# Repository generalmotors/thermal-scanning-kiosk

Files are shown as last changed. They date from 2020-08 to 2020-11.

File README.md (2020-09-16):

## title: Thermal Scanning Kiosk

# Overview and Context

In this paper, we present a low-cost thermal scanning kiosk for identifying
higher temperature individuals entering a facility. The kiosk offers
conveniences, such as auto-start and auto-reset, which eliminates the need for a
user to touch the kiosk.

This kiosk is not intended to measure actual temperature nor is it for the
diagnosis of any medical condition such as COVID-19 or any other disease. It
does not determine if the user has a fever nor does it provide the user with
their temperature. Rather, the device works by comparing thermal readings from a
current user with an average of readings from prior users. If the present user’s
reading is a certain amount away from the average, the user is presented with a
display recommending further evaluation. To determine whether someone may be
febrile, your facility then must make provisions to take body temperature
measurements with an appropriate evaluation method such as a non-contact
infrared thermometer or a clinical grade contact thermometer.

This kiosk is designed to use the FLIR E8-XT model infrared camera from FLIR®
Systems, Inc. Along with this document, we provide two versions of software that
incorporate FLIR software: a compiled, ready-to-use version and a source code
version. The ready-to-use version requires acceptance of FLIR’s software license
terms. The source code version references FLIR’s SDK which requires accepting
FLIR’s terms of use. We also provide plans for 3D printing parts used in
construction of the kiosk to hold the E8-XT camera in place.

Licenses for use of the intellectual property we provide are included. These
licenses place certain restrictions on the use of this intellectual property
including that this intellectual property can only be used in a kiosk of the
type described here and that this intellectual property may not be used for
commercial purposes. In other words, you cannot use this intellectual property
to market or sell a kiosk or to manufacture a kiosk for third parties.

This document provides a description of what you need to get this kiosk up and
running. Simplicity, portability, and cost were goals for this effort. We hope
that it will not only be used by the community at large but that it will be
improved upon by others.

# Capabilities

The kiosk provides the following capabilities:

-   A physical kiosk comprised of a height-adjustable stand, VESA-mountable LCD
    screen with built in web camera and speakers, Windows PC, infrared camera,
    USB hub and power connections

-   Efficient evaluation which averages as little as 1 to 3 seconds per user

-   Thermal evaluation based on an automatic rolling temperature that can
    account for ambient changes over time

-   An Area of Interest for thermal temperature measurement is automatically
    identified and set to upper face and head including the tear ducts and
    forehead. Facial detection initiates automatic evaluation function when a
    person steps up to the unit

-   Automatic distance compensation to accommodate distance range of 2 ft to 4.5
    ft from the camera for consistent measurements

-   Automatic completion of kiosk flow when a person steps away from the unit

-   Facial detection will work with face mask either on or off

-   On-screen notification to remind the user to remove a hat or glasses

-   Measured temperature is not displayed to each user and instead the user sees
    only a PASS/FAIL result

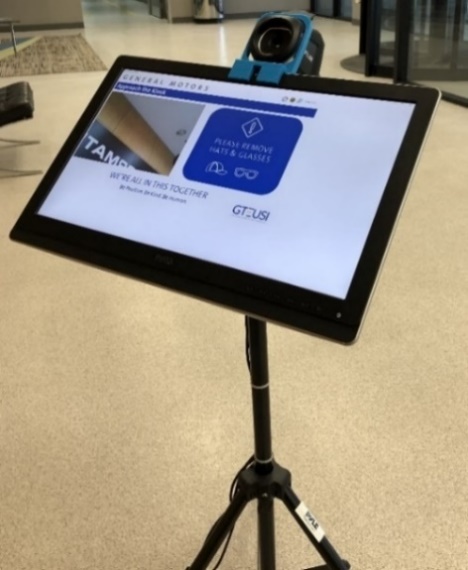
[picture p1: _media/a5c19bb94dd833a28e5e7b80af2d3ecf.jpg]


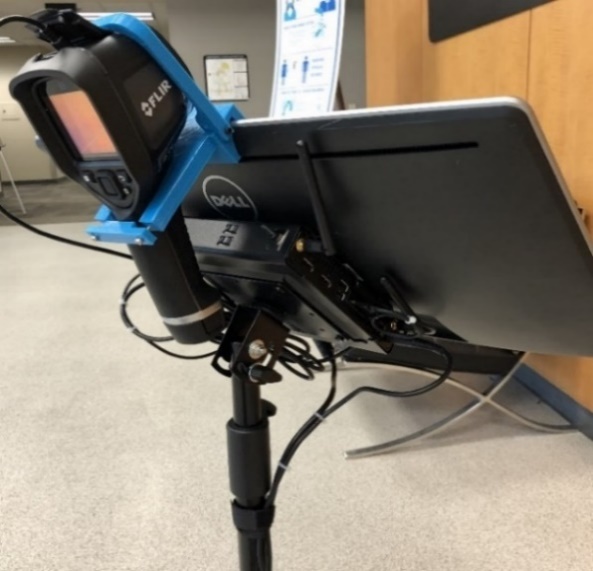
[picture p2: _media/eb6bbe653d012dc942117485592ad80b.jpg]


# Bill of Materials

The following components are used to build the kiosk and are referenced in the
architecture and implementation sections that follow.

| **Component Description**                | **Qty** | **Approx. Cost** |
|------------------------------------------|---------|------------------|
| FLIR E8-XT Thermal Camera                | 1       | \$5,000          |
| HP ProDesk 400 G5 Mini (1 HDMI port)     | 1       | \$510            |
| HP V2 Mounting Kit (Mini Desktop)        | 1       | \$35             |
| Dell 21.5” Monitor (UZ2215Hf)            | 1       | \$140            |
| HDMI 1.5 ft cable                        | 1       | \$7              |
| Pyle VESA Flat Screen Tripod (100 x 100) | 1       | \$40             |
| USB A/B Cable 1.5ft (to screen)          | 1       | \$6              |
| USB A/Micro USB Cable 1.5ft (to camera)  | 1       | \$6              |
| 1" Cable Management Sticker              | 1       | \$0.25           |
| 4" Zip Tie                               | 8       | \$1              |
| 8" Zip Tie                               | 8       | \$1              |
| 11" Zip Tie                              | 8       | \$1              |
| 3D Printed Camera Bracket (4 parts)      | 1       | \$0              |
| 3D Printed Gasket                        | 1       | \$0              |
| M3 x 14mm screws                         | 7       | \$5              |
| M3 nuts                                  | 2       | \$0.25           |
| Inland USB 3.1 Hub                       | 1       | \$15             |
| Power strip (6 port)                     | 1       | \$10             |
| **Total Cost**                           |         | \$5,777.50       |

Architecture

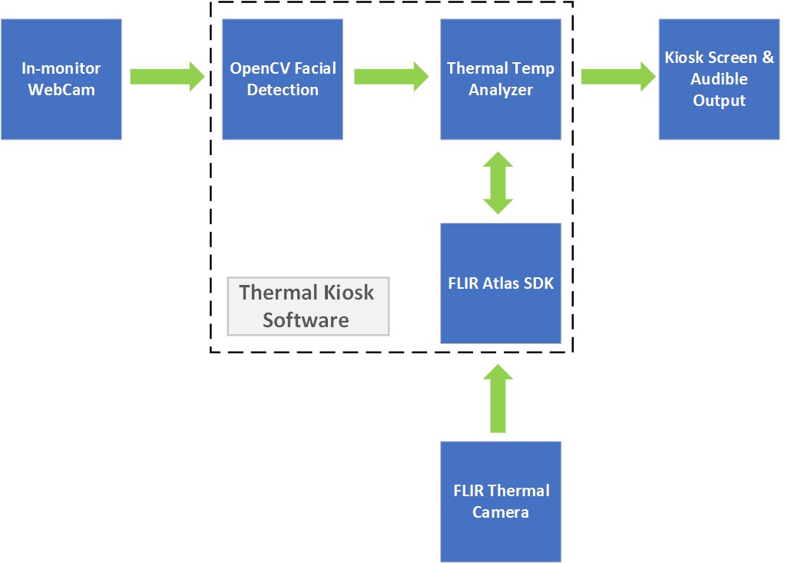
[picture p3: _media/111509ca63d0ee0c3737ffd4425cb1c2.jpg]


The system uses OpenCV facial detection to start the evaluation process and
identify the location of the user’s face. Using this location, the system sets
the Area of Interest (AoI) to include the upper face and head which includes the
tear ducts and forehead. The system retrieves multiple thermal temperature
assessments for each user from the FLIR E8-XT via the FLIR Atlas SDK. The system
averages the individual user samples and compares the user's average against a
rolling average of the past 15 users.

# Flow

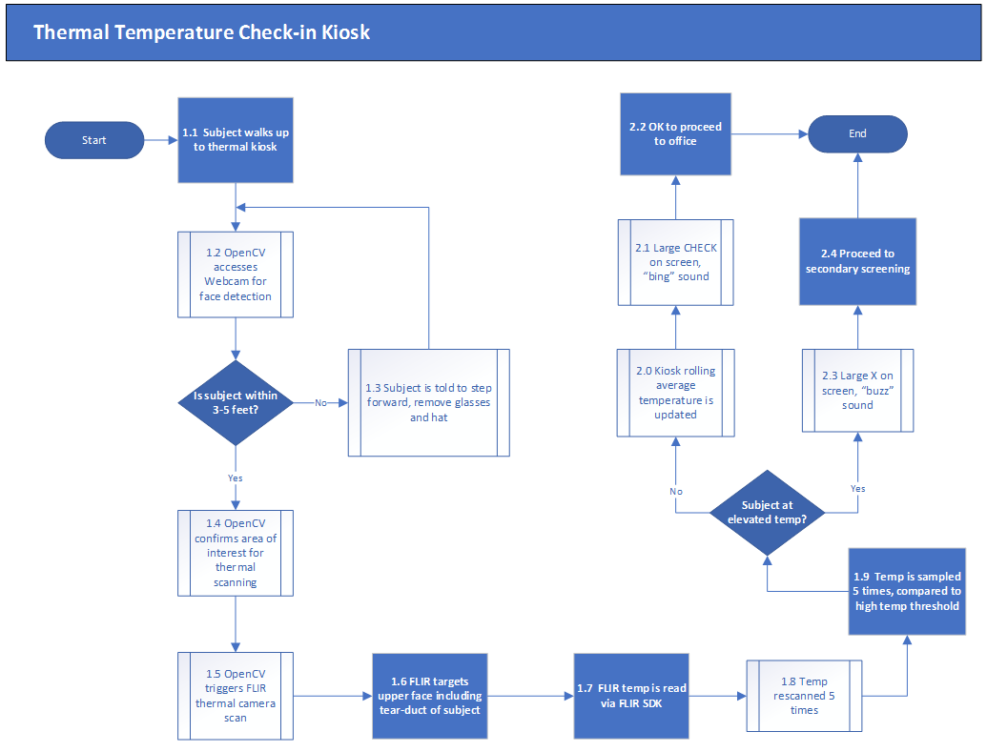
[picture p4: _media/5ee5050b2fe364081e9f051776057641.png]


# Thermal Process Details

## Thermal Image Retrieval

OpenCV analyses the web camera video feed at 30 FPS to identify faces within an
acceptable distance range for evaluation. If the user is too far away,
instructions are displayed to prompt the user to move closer. If multiple users
are identified, instructions are displayed to indicate that only one person at a
time may use the system and the system will not initiate evaluation in this
condition. Once OpenCV establishes a qualified facial detection within the
specified distance range, the evaluation process will be triggered and the first
thermal base image will be retrieved from the FLIR E8-XT camera using the
FLIR.Atlas.Live library (FLIR Atlas SDK 5.0). If the user moves out of the frame
or out of the specified distance range during evaluation, the process will halt,
discard any completed sampling measurements, and reset the process such that the
user will need to re-establish a qualified facial detection to initiate
evaluation again from the beginning.

## Area of Interest

Upon qualified facial detection by OpenCV, coordinates of the user’s face are
established and a rectangle around the user’s face is identified. The rectangle
coordinates are processed to identify the Area of Interest (AoI) which targets
the user’s upper face and forehead while also avoiding gaps above and below the
user’s ears.

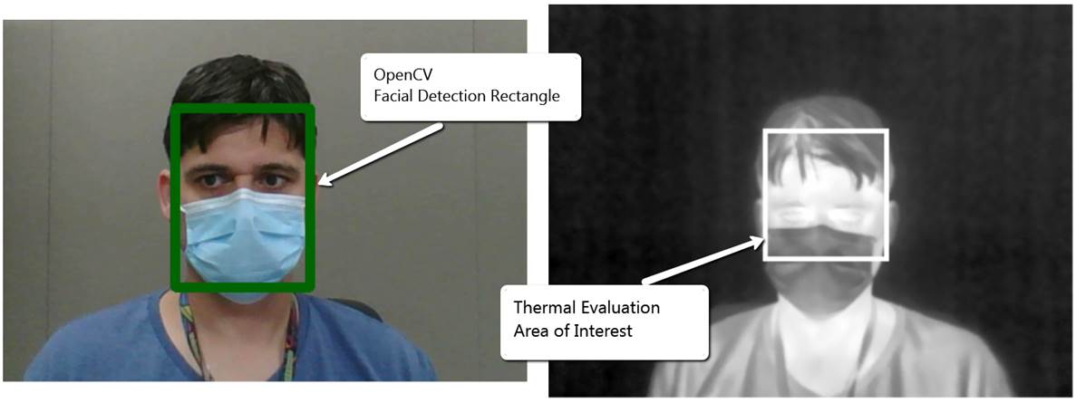
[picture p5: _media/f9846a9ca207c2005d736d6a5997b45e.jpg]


Image compensation is applied to the web camera image and the thermal image to
account for the physical offset and angle differences between the two cameras.
Angle distance compensation is applied to the image alignment to correct the
alignment over a user distance range between 2ft to 4.5ft.

The Area of Interest is calculated and applied to the thermal base image based
on a percentage of the OpenCV Facial Detection Rectangle in order to focus the
thermal evaluation on the user’s upper face and forehead. The following
configurable values in the app.config file determine the percentage for the Area
of Interest

*\<add key="irHeightAoI" value="0.65" /\>* -- *(Top 65% of the user’s face /
head)*  
*\<add key="irWidthAoI" value="0.9" /\>* -- *(90% centered width)*

## User Sampling and Averaging

While the user maintains a qualified facial detection, five (5) sequential
thermal base image samples are taken by the FLIR E8-XT infrared camera. The
thermal measurement is acquired from the thermal base image by using the
FLIR.Atlas.Image library (FLIR Atlas SDK 5.0) to locate the highest temperature
within the designated Area of Interest. Once the existing thermal base image is
processed, the highest temperature reading within the Area of Interest is stored
in memory and the thermal image is discarded. A new thermal image is then
retrieved using the FLIR.Atlas.Live library (FLIR Atlas SDK 5.0) and the Area of
Interest is re-calculated using the corresponding facial detection coordinates
from OpenCV. This compensates for the user’s movement throughout the evaluation
process. If the user moves out of the frame or out of the acceptable distance
range before the system completes all five samples, the process will reset,
existing samples will be discarded, and the user will need to establish a
qualified facial detection to re-start the evaluation process from the
beginning.

Once five (5) samples have been collected, the results are averaged to produce
the determinant thermal value for the user’s session. This value is compared to
the rolling baseline average of the past fifteen (15) users to determine the
pass / fail outcome of the current user’s session.

The number of required samples is configurable in the app.config file using the
following parameter:

*\<add key="requiredScanPasses" value="5" /\>* -- *(5 samples will be required
for each user)*

## Rolling Baseline Average

The baseline rolling average is determined by the average of the determinate
thermal outcomes (average of five (5) samples per user) for the previous fifteen
(15) successful evaluation sessions. Failed outcomes are excluded from the
rolling average calculation which prevents users with elevated temperatures from
artificially skewing the rolling average upwards.

The rolling baseline average is calculated by holding in memory the determinant
thermal result value for the previous fifteen (15) passing evaluation sessions.
When a new successful passing scan is completed, the oldest result is removed
from memory and the new result is committed to memory. The new rolling baseline
average is then calculated based upon the current fifteen values in memory.

The number of evaluation results to include in the rolling average is
configurable in the app.config file using the following parameter.

*\<add key="runningAvgUserCount" value="15" /\> -- (Average the most recent 15
evaluation results)*

## User Analysis

The determinant thermal value for the user’s session is compared to the Rolling
Baseline Average.

If the user’s determinant thermal value is within the defined variance from the
current rolling baseline average, then the user will receive a Pass notification
and user’s determinant thermal value will be used to update the Rolling Baseline
Average.

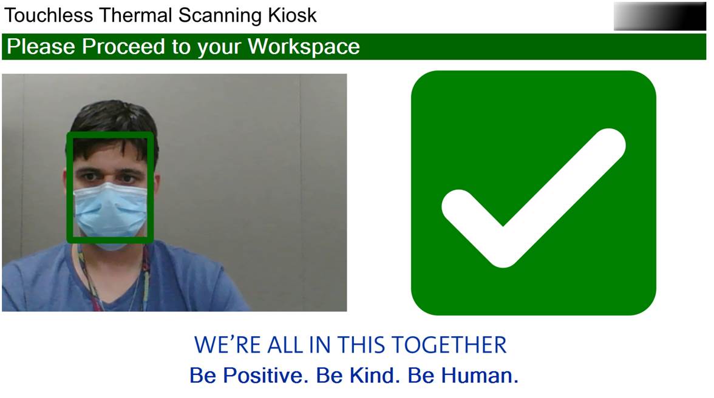
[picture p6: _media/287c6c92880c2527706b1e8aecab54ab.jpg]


If the user’s determinant thermal value is NOT within the defined variance from
the current rolling baseline average, then the system will initiate a second
evaluation for the user which will collect a full set of five (5) additional
samples as defined by the *"requiredScanPasses"* parameter. If the second
evaluation also falls outside of the defined variance, then the user will
receive a Fail notification and the Rolling Baseline Average will not be
updated.

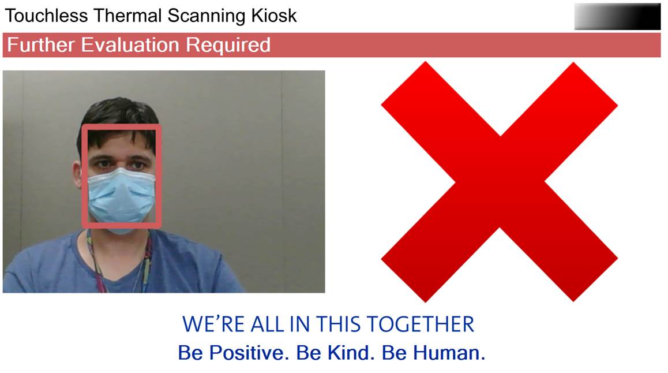
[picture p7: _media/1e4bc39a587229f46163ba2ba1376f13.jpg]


The defined variance is configurable in the app.config file using the following
parameters.

*\<add key="highTempThreshold" value="4.0" /\>* -- *(Allow 4 degrees F above the
rolling baseline average*)  
*\<add key="lowTempThreshold" value="6.0" /\>* -- *(Allow 6 degrees F below the
rolling baseline average)*

# Implementation

Instructions for assembling and setting up a kiosk are provided in the Thermal
Scanning Kiosk Installation and Setup Guide. Please have a USB keyboard and USB
mouse available for software download and setup. We recommend two people for the
assembly process. Safety glasses should be worn during preparation and assembly.

The kiosk uses 3D printed materials. Plans for these components are located at
https://github.com/generalmotors/thermal-scanning-kiosk/blob/master/3D-Printed-Parts/.
Commercial 3D printing services may be used to print these parts.

-   Suggested 3D Print Specs

    -   Material: PLA

    -   Layer Height: 0.3mm

    -   Wall Thickness: 1.2mm

    -   Top / Bottom Thickness: 1.2mm

    -   Infill: 25% to 30%

As shown below, four components on the left are used to make the camera bracket.
The part on the right is VESA gasket.

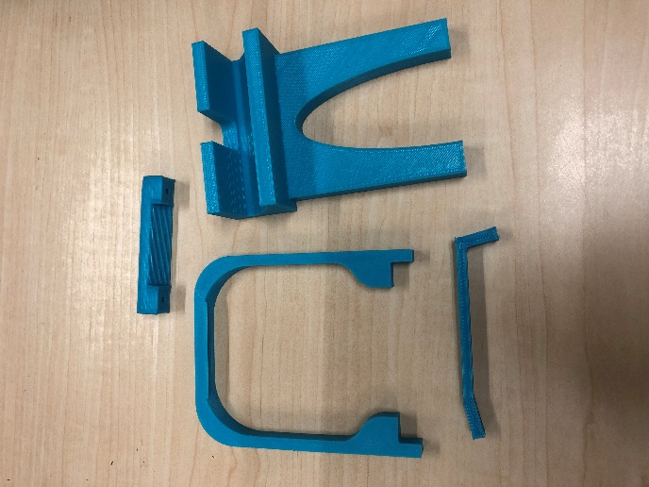
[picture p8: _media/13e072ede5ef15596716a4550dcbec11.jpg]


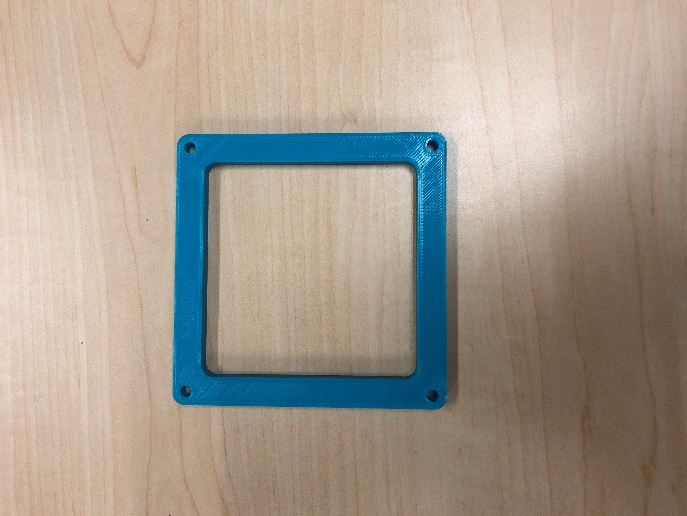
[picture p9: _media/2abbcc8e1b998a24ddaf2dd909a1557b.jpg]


The physical cabling and basic hardware layout are generally illustrated in the
following two diagrams.



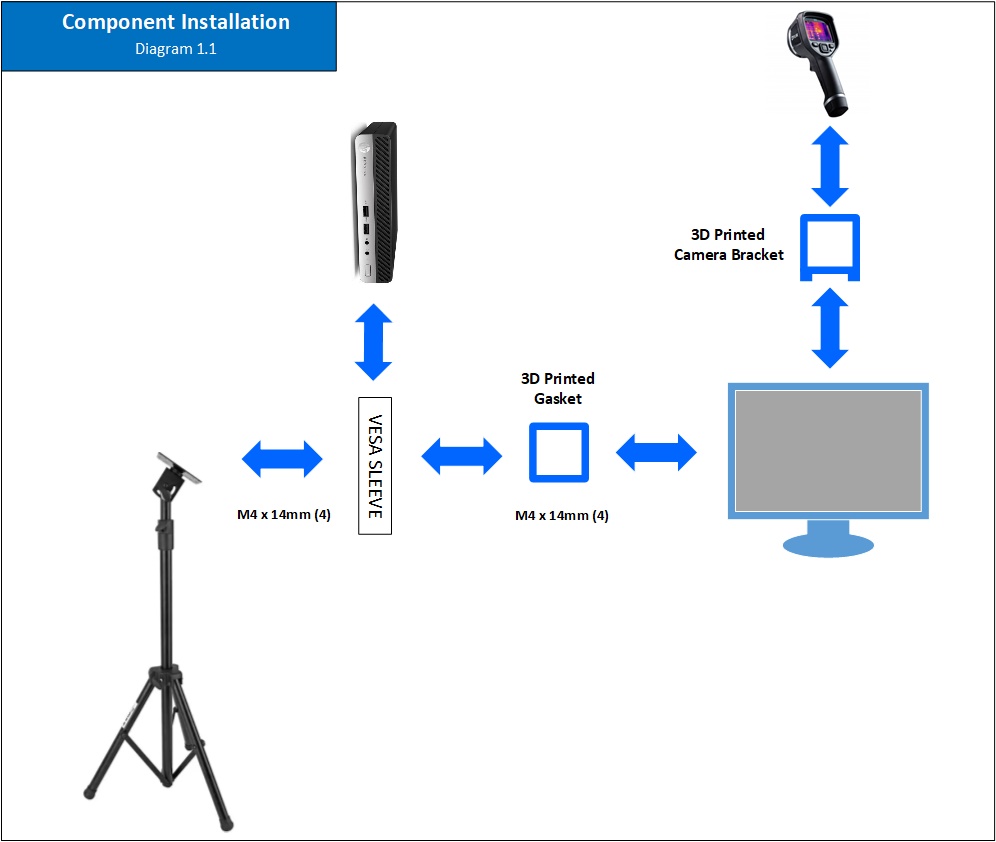
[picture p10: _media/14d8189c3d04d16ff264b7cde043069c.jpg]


# Environmental Considerations

Below are steps that could help obtain accurate and consistent thermal
measurements from the kiosk.

-   Position the kiosk so that the camera is pointed away from outside windows
    and direct sunlight.

-   Locate the kiosk in an area with a consistent ambient temperature that is
    not influenced by temperature changes such as an external doorway. We do not
    recommend using the kiosk in a warehouse environment due to temperature
    inconsistencies.

-   The camera should be at room temperature. The E8 Manual states “For very
    accurate results, we recommend that you wait 5 minutes after you have
    started the camera before measuring a temperature.”

-   We recommend something behind the scanning area to block unwanted heat
    sources such as HVAC outlets, external windows or ceiling lights. This could
    be, for example, a wall or a backdrop.

    -   If you are using a backdrop, place the backdrop about 6 feet (2 meters)
        from the kiosk to allow a user to stand approximately 3-5 feet (1-1.5
        meters) away from the kiosk for evaluation.

    -   You can make a backdrop such as the one illustrated below. The frame is
        constructed of pipe or PVC that is anchored in 5 gallon weighted buckets
        (sand). The dimensions of the frame should exceed the kiosk’s field of
        view (this backdrop is about 8 feet by 8 feet). A colored piece of
        fabric may be placed over the frame and held in place with pins or
        clips. Make sure the backdrop is stable and not a trip hazard.

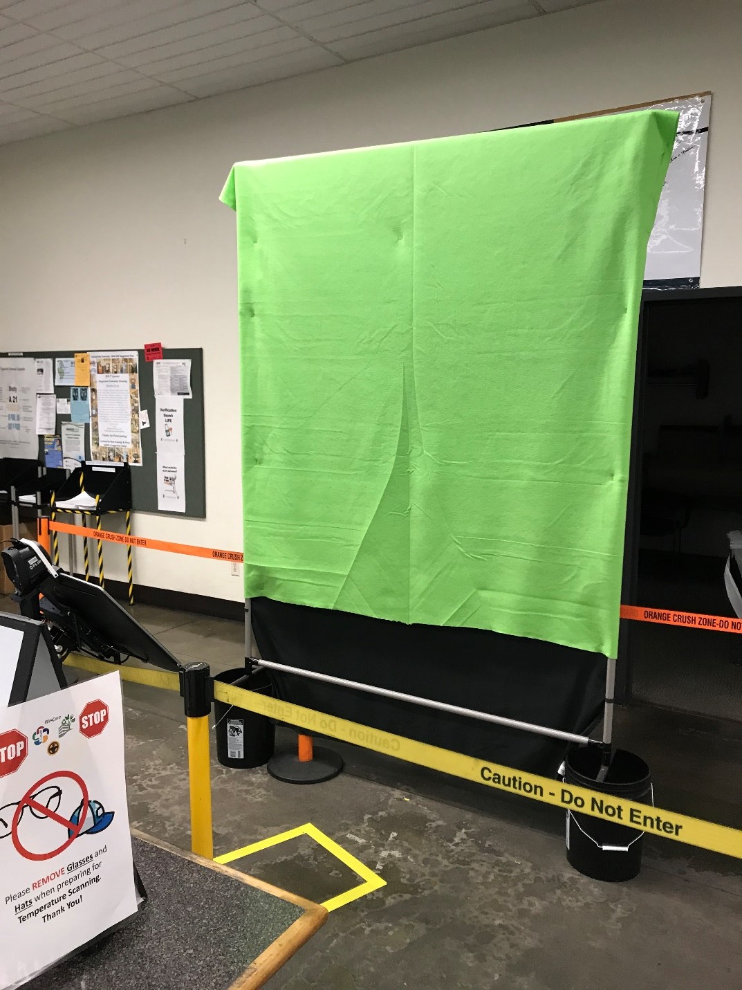
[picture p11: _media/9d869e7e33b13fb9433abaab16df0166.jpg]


-   The scanning area should have enough light to ensure the contours of the
    scanned subject face are recognized. An external LED source can be added to
    provide additional light with a minimum of introduced heat.

# Compiled Software Distribution

A compiled distribution is available for simple setup and operation. This
version of the software will only work with a FLIR E8 camera. Custom code
modifications are not available with this option. However, logos and system
operating parameters may be edited as described in the Software Customization
Features section below.

The compiled distribution is provided as an .msi installation file, which is at
the following location:
<https://github.com/generalmotors/thermal-scanning-kiosk/blob/master/_distribution/ThermalScanningKiosk_setup.msi>.
This installation includes a setup wizard that will provide the full software
implementation. You will need to accept license terms during the installation.

The compiled distribution includes FLIR libraries which are licensed separately
by FLIR. Agreeing to the FLIR software license is required during installation
to proceed with the installation and to use the kiosk software with the FLIR
E8-XT camera.

# Source Code Package

The source code may be customized using an IDE for C\# .Net Windows Forms
applications. The source code is dependent on FLIR Libraries located in the
Atlas SDK Version 5.0. The FLIR SDK is licensed separately and may be retrieved
from FLIR. Instructions to obtain the FLIR SDK are available at
<https://flir.custhelp.com/app/answers/detail/a_id/1275>.

After completing the installation of the FLIR SDK, copy all library files into
the ThermalScanningKiosk project within the IDE. Ensure that all FLIR library
files are added to the project and set to copy to the output directory on
compile. The source code package already includes references and directives to
the FLIR Libraries, but the program will not compile and will not run properly
until the FLIR Libraries are included in the project and added to the output
directory on compile.

# Software Customization Features

The software has many customizable fields such as the custom audible alerts,
modifications to temperature thresholds and the number of scans. You can also
customize the messaging for pass/fail scenarios and bring in your own
organizational branding.

The configuration file can be found at

*...\\Program Files\\ThermalScanningKiosk\\ThermalScanningKiosk.exe.config*
under the \<appSettings\> header.

Customizable settings include the following:

-   **Audible Alerts** – The software uses the default Windows sounds. To add
    your own, ensure the file is in .wav format and add it to the HP ProDesk
    Mini. Edit the file location under the passSoundPath/failSoundPath in the
    config file for the file location.

-   **Threshold Adjustment** -- The default value is 4F / 6F as the temperature
    variance, this can be modified under the highTempThreshold/lowTempThreshold
    in the config file.

-   **Scans per user** -- The default value is 5 scans per user, this can be
    modified under the requiredScanPasses in the config file.

-   **Organizational branding on screen** -- Ensure the file is .jpg or .png
    format and add to the …\\ThermalScanningKiosk\\Graphics\\ folder. Be sure to
    update the file name in the config file.

-   **Rolling Average Temperature** -- The rolling average is based on the last
    15 scanned users. The number of users can be increased/decreased under the
    runningAvgUserCount in the config file.

# Terms of Use

By using this kiosk design and its associated software, you agree to the
following:

-   This kiosk design and its associated software may only be used for initial
    evaluation of multiple users entering a facility or other area.

-   This kiosk design and its associated software can only be used to examine
    one user at a time.

-   This kiosk design and its associated software will not be used to determine,
    diagnose or treat any disease or condition, including COVID-19.

-   This kiosk design and its associated software will not be used to determine
    if a user has a fever.

-   This kiosk design and its associated software will not be used to provide a
    user with their temperature, or any number related to their temperature.

-   This kiosk design and its associated software must notify a user when an
    elevated thermal measurement is determined and, if such a determination is
    made, that additional evaluation is required.

-   This kiosk design and its associated software can only be used in an
    environment where further evaluation is available using an appropriate
    method, such as measurement with a non-contact infrared thermometer or a
    clinical grade contact thermometer.

-   This kiosk design and its associated software cannot be used for a
    commercial purpose. This includes manufacturing a kiosk for a third party;
    marketing or selling a kiosk; requesting compensation for the use of a
    kiosk; renting or leasing a kiosk; and the like. This does not preclude you
    using the kiosk design and its associated software for internal use with
    employees, visitors, customers, students, and the like who may enter your
    facility.

-   FLIR requires that the use of this App with a FLIR EST Camera or approved
    FLIR Device is intended for use only as a skin temperature measuring tool,
    and is not a medically-approved body temperature measurement device or a
    medical diagnostic tool.

This kiosk relies on a third-party thermal infrared camera to provide readings
to the software. An appropriate camera must be selected and any instructions for
the camera followed for proper functioning of the kiosk. FLIR has indicated that
its E8 camera is generally suitable for skin temperature screening applications.

THIS KIOSK DESIGN AND ITS ASSOCIATED SOFTWARE ARE PROVIDED "AS IS", WITHOUT
WARRANTY OF ANY KIND, EXPRESS OR IMPLIED, INCLUDING BUT NOT LIMITED TO THE
WARRANTIES OF MERCHANTABILITY, FITNESS FOR A PARTICULAR PURPOSE, AND
NONINFRINGEMENT. IN NO EVENT SHALL THE AUTHORS OR COPYRIGHT HOLDERS BE LIABLE
FOR ANY CLAIM, DAMAGES, OR OTHER LIABILITY, WHETHER IN AN ACTION OF CONTRACT,
TORT OR OTHERWISE, ARISING FROM, OUT OF, OR IN CONNECTION WITH THE KIOSK,
SOFTWARE, OR THEIR USE.

# Acknowledgement

This thermal kiosk represents the hard work of some very passionate and
innovative people at General Motors. While many people contributed, we would
like to call out the core team specifically:

-   Spencer Searle

-   James Currie

-   Christopher Reeves

-   Naveen Sankar

-   Paerhati Remutula

-   Mike Schuplin

-   Peter Linton

-   Dan Rudman

-   Shane McCutchen

-   Peter Wyatt

-   Joe Gleason

# License

The software described in this paper is offered under licenses at
<https://github.com/generalmotors/thermal-scanning-kiosk/blob/master/LICENSE.txt>.



This documentation is licensed under a [Creative Commons
Attribution-NoDerivatives 4.0 International
License](https://creativecommons.org/licenses/by-nd/4.0/). 



Designs for the 3D-printed camera bracket and 3D-printed gasket described in
this documentation are licensed under a [Creative Commons Attribution-ShareAlike
4.0 International License](https://creativecommons.org/licenses/by-sa/4.0/).

Attribution: Copyright 2020 General Motors LLC

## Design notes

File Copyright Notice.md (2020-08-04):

Designs for the 3D-printed camera bracket and 3D-printed gasket included in this
distribution are

(c) General Motors LLC.

The Thermal Scanning Kiosk software package (Executable Version) and the Thermal
Scanning Kiosk software package (Source Code Version) are (c) General Motors
LLC. Both software packages also contain code from other parties, including:

1. FLIR Atlas Software Development Kit (SDK), which is (c) FLIR Systems, Inc.;
and

2. OpenCV, which is (c) OpenCV team and the respective copyright holders, below.

Copyright (C) 2000-2020, Intel Corporation, all rights reserved.

Copyright (C) 2009-2011, Willow Garage Inc., all rights reserved.

Copyright (C) 2009-2016, NVIDIA Corporation, all rights reserved.

Copyright (C) 2010-2013, Advanced Micro Devices, Inc., all rights reserved.

Copyright (C) 2015-2016, OpenCV Foundation, all rights reserved.

Copyright (C) 2015-2016, Itseez Inc., all rights reserved.

Copyright (C) 2019-2020, Xperience AI, all rights reserved.

Copyright (C) 2019, shimat

Copyright (C) 2020, General Motors LLC

Third party copyrights are property of their respective owners.

Redistribution and use in source and binary forms, with or without modification,

are permitted provided that the following conditions are met:

\* Redistributions of source code must retain the above copyright notice,

this list of conditions and the following disclaimer.

\* Redistributions in binary form must reproduce the above copyright notice,

this list of conditions and the following disclaimer in the documentation

and/or other materials provided with the distribution.

\* Neither the names of the copyright holders nor the names of the contributors

may be used to endorse or promote products derived from this software

without specific prior written permission.

This software is provided by the copyright holders and contributors "as is" and

any express or implied warranties, including, but not limited to, the implied

warranties of merchantability and fitness for a particular purpose are
disclaimed.

In no event shall copyright holders or contributors be liable for any direct,

indirect, incidental, special, exemplary, or consequential damages

(including, but not limited to, procurement of substitute goods or services;

loss of use, data, or profits; or business interruption) however caused

and on any theory of liability, whether in contract, strict liability,

or tort (including negligence or otherwise) arising in any way out of

the use of this software, even if advised of the possibility of such damage.

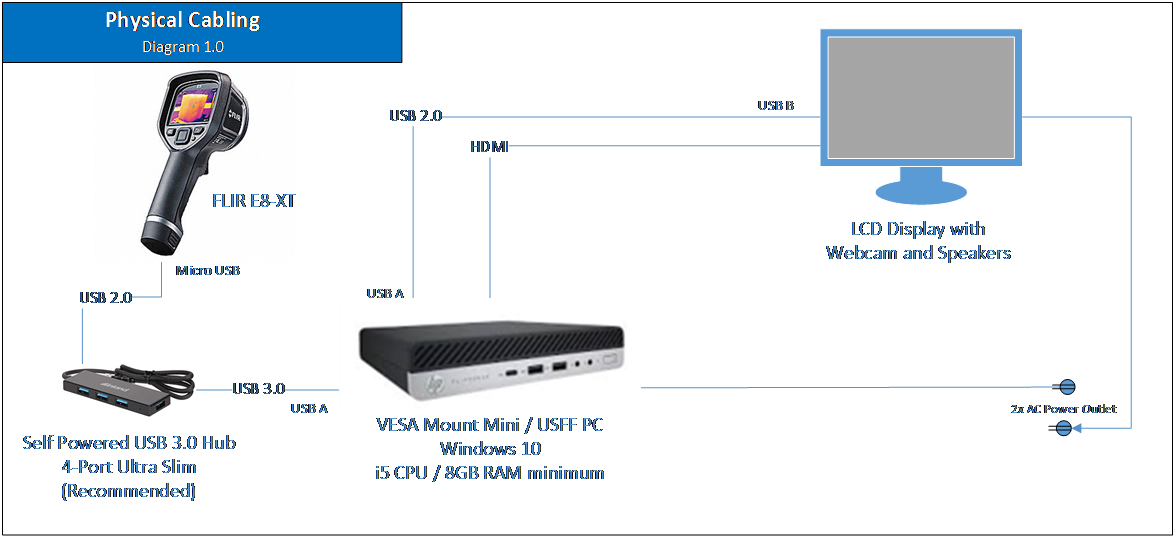
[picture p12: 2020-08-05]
_media/5ee5050b2fe364081e9f051776057881.png

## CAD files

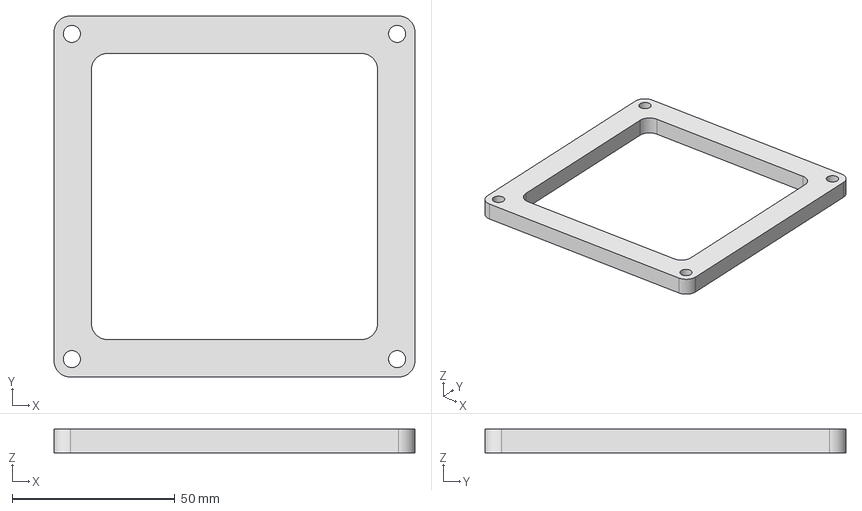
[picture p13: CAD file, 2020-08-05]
3D_Printed_Parts/Camera_Mount_Dell_UZ2215HF/VESA_Gasket.stp
111.0 x 111.0 x 7.25 mm

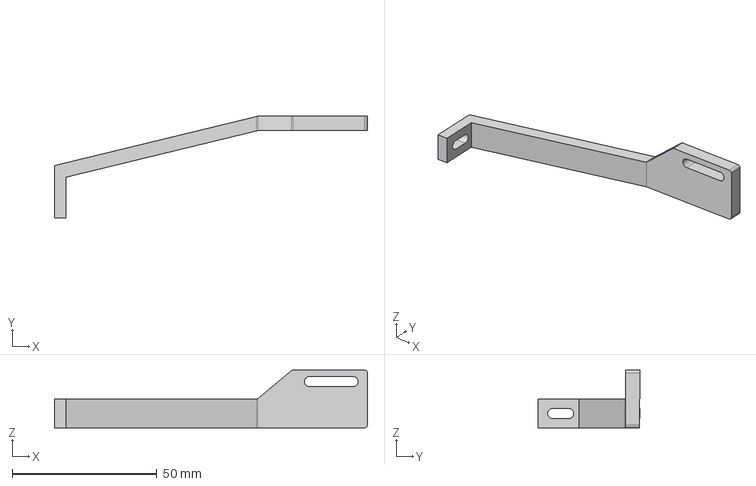
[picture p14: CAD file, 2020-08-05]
3D_Printed_Parts/Camera_Mount_HP_E240c/Camera_mount_HP_E240c_Side.stp
108.0 x 35.0 x 20.0 mm

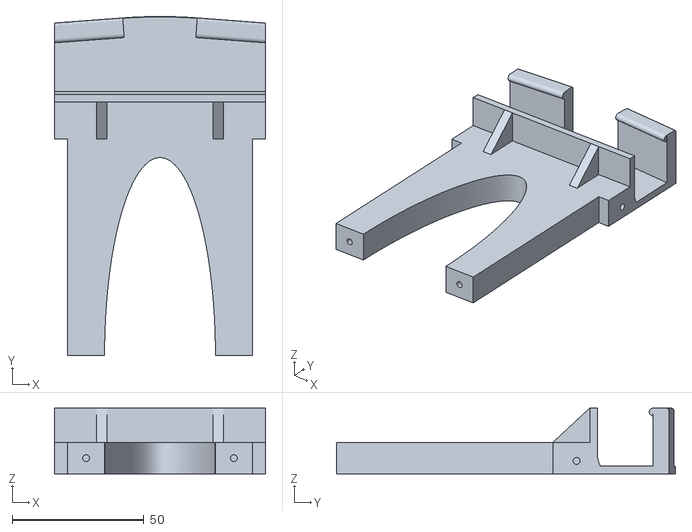
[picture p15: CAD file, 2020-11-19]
3D_Printed_Parts/Camera_Mount_HP_LA2206xc/Camera_Mount_HP_LA2206xc_Body.stl
80.0 x 128.5 x 25.0

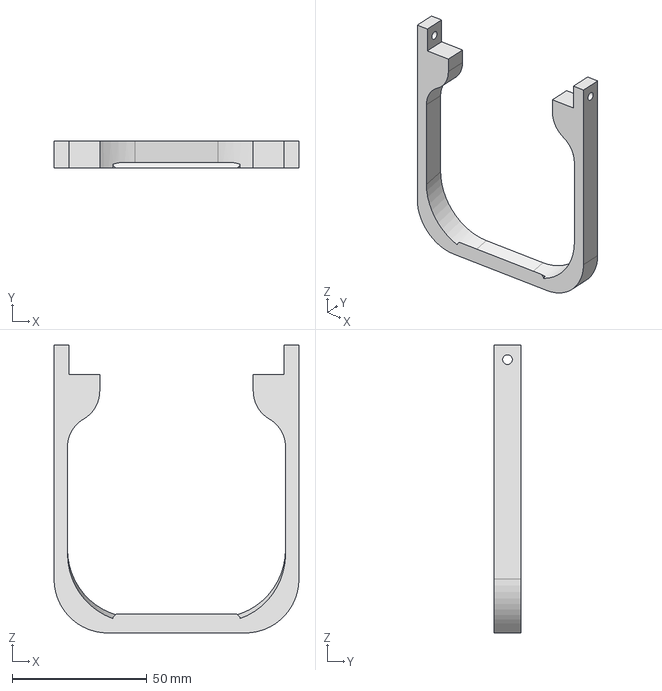
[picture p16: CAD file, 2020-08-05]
3D_Printed_Parts/Camera_Mount_Universial/Camera_mount_Universial_Top_107mm.stp
91.0 x 10.0 x 107.0 mm

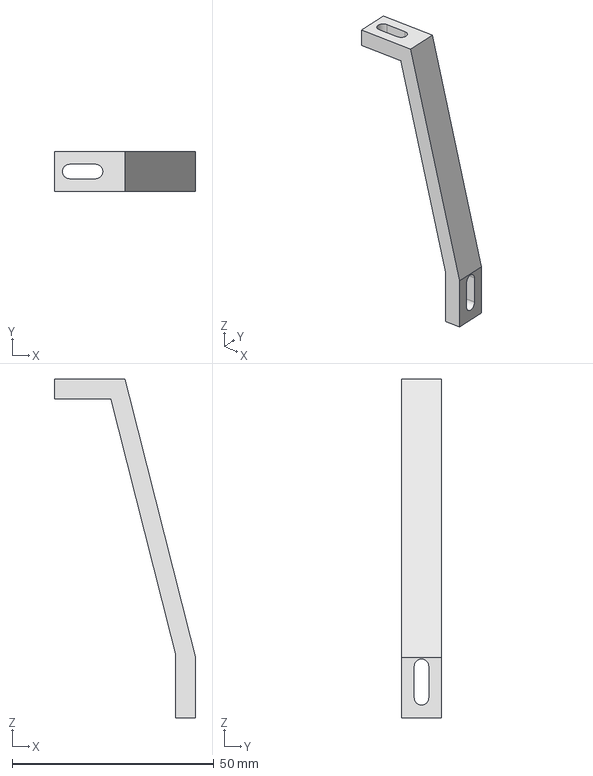
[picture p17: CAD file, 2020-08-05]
3D_Printed_Parts/Camera_Mount_Dell_UZ2215HF/Camera_mount_Dell_UZ2215HF_Side.stp
35.0 x 10.0 x 84.0 mm

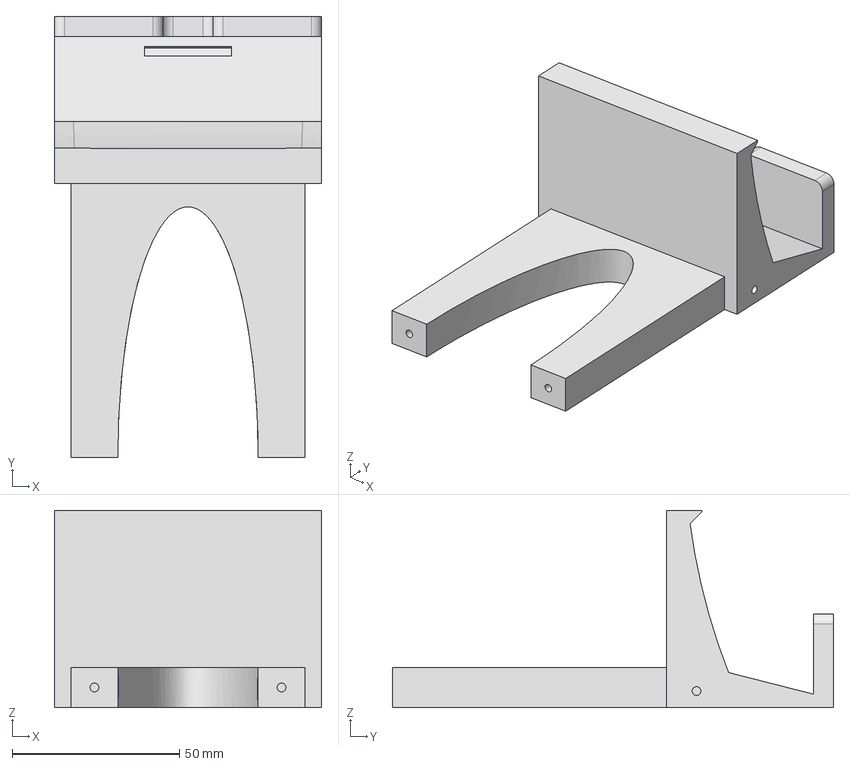
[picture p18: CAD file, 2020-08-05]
3D_Printed_Parts/Camera_Mount_HP_E240c/Camera_mount_HP_E240c_Body.stp
80.0 x 132.0 x 59.0 mm

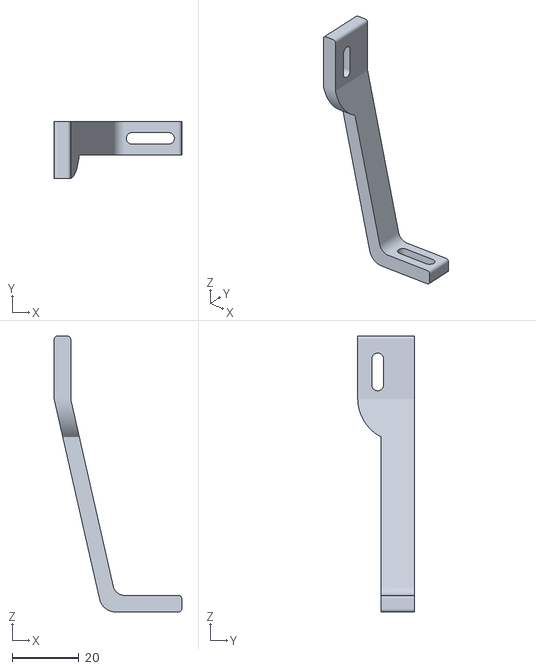
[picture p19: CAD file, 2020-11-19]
3D_Printed_Parts/Camera_Mount_HP_LA2206xc/Camera_Mount_HP_LA2206xc_Side.stl
38.4 x 17.0 x 83.0

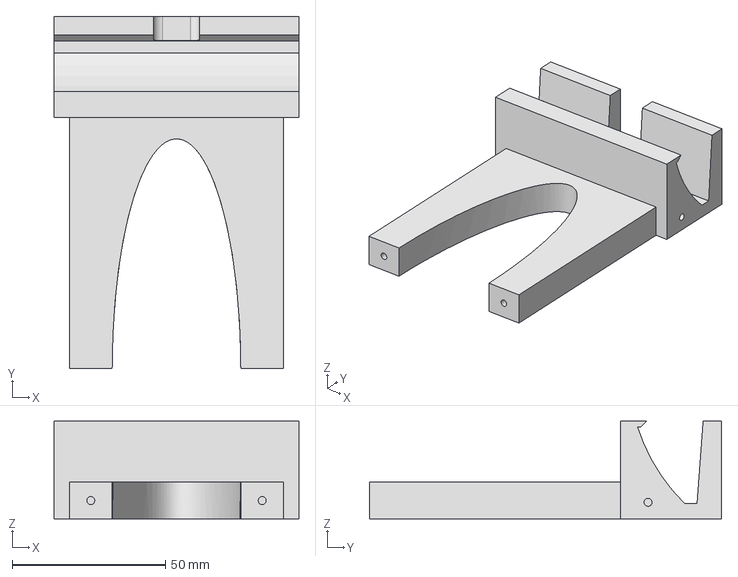
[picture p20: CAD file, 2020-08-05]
3D_Printed_Parts/Camera_Mount_Dell_UZ2215HF/Camera_mount_Dell_UZ2215HF_Body.stp
80.0 x 115.0 x 32.0 mm

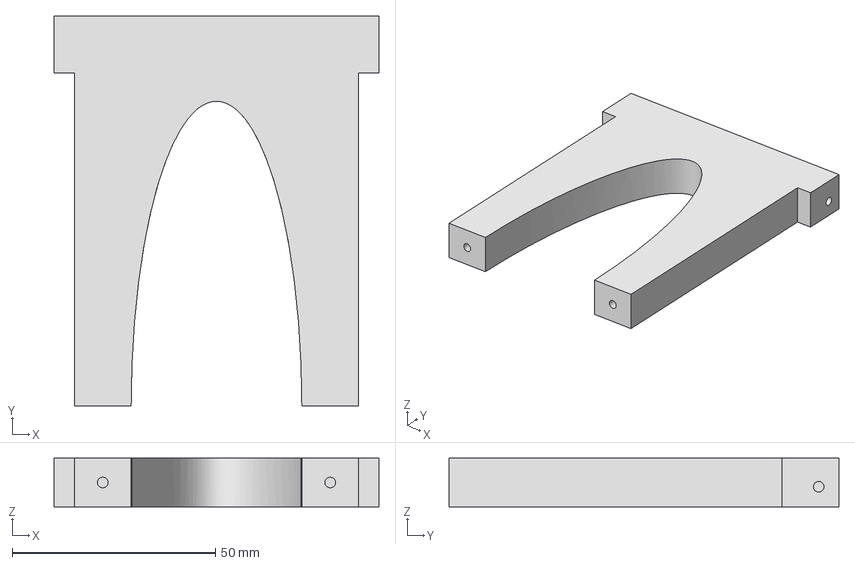
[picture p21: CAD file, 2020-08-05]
3D_Printed_Parts/Camera_Mount_Universial/Camera_mount_Blank_Body.stp
80.0 x 96.0 x 12.0 mm

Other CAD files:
3D_Printed_Parts/Camera_Mount_Universial/Camera_mount_Universial_Top_109mm.stp
3D_Printed_Parts/Camera_Mount_Universial/Camera_mount_Universial_Top_112mm.stp
3D_Printed_Parts/Camera_Mount_Universial/Camera_mount_Universial_Top_111mm.stp
3D_Printed_Parts/Camera_Mount_Universial/Camera_mount_Universial_Top_108mm.stp
3D_Printed_Parts/Camera_Mount_Universial/Camera_mount_Universial_Top_110mm.stp
3D_Printed_Parts/Camera_Mount_Dell_UZ2215HF/Camera_mount_Dell_UZ2215HF_Body.stl
3D_Printed_Parts/Camera_Mount_Dell_UZ2215HF/Camera_mount_Dell_UZ2215HF_Side.stl
3D_Printed_Parts/Camera_Mount_Dell_UZ2215HF/VESA_Gasket.stl
3D_Printed_Parts/Camera_Mount_HP_E240c/Camera_mount_HP_E240c_Body.stl
3D_Printed_Parts/Camera_Mount_HP_E240c/Camera_mount_HP_E240c_Side.stl
3D_Printed_Parts/Camera_Mount_Universial/camera_mount_Universial_Top_107mm.stl
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

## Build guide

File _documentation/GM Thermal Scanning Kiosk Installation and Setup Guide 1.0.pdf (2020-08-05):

## Thermal Scanning Kiosk Installation and Setup Guide

This Guide is intended to provide instructions to assemble the thermal evaluation kiosk, adjust the camera, how to use and basic troubleshooting. The initial build includes the use of power tools and manually assembling the kiosk. Assembly can take 30 to 60 minutes per kiosk.

We recommend two people for the assembly process.

Safety glasses should be worn during assembly.

This Guide is intended to supplement the readme file. Please read that file first.

## 1. SUGGESTED TOOLS

1.1 Drill (Corded or Cordless)
1.2 3/16 Allen key
1.3 1/2-inch wrench
1.4 1/8-inch drill bit
1.5 3/32 drill bit
1.6 5mm wrench
1.7 Phillips screwdriver #2

## 2. VESA TRIPOD ASSEMBLY

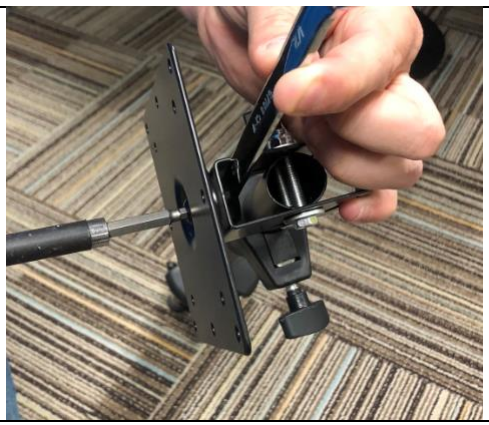
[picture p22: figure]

2.1 Tighten the tripod VESA mount rotational joint with the 3/16 Allen key and half inch wrench

2.2 Drill VESAGasket holes (4) with a 1/8 inch drill bit

NOTE: HP monitors do not require this gasketso no drilling is required

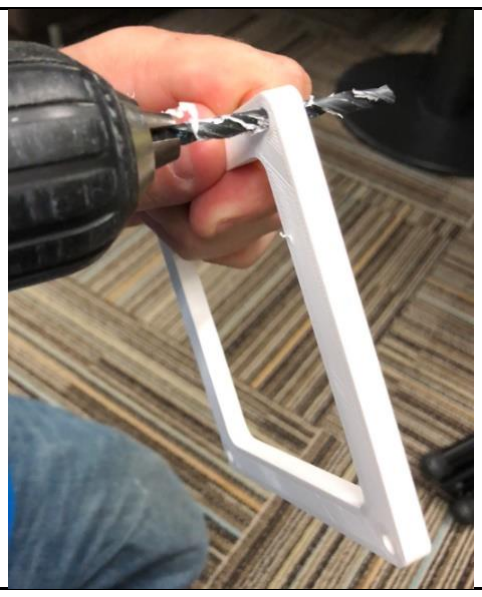
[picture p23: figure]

2.3 Place VESA gasket on the back of the monitor, set VESA sleeve on top and use the M4 Philip head screws provided in the VESA sleeve kit.
2.3.1 | Hand tighten screws then use Phillips screwdriver to tighten

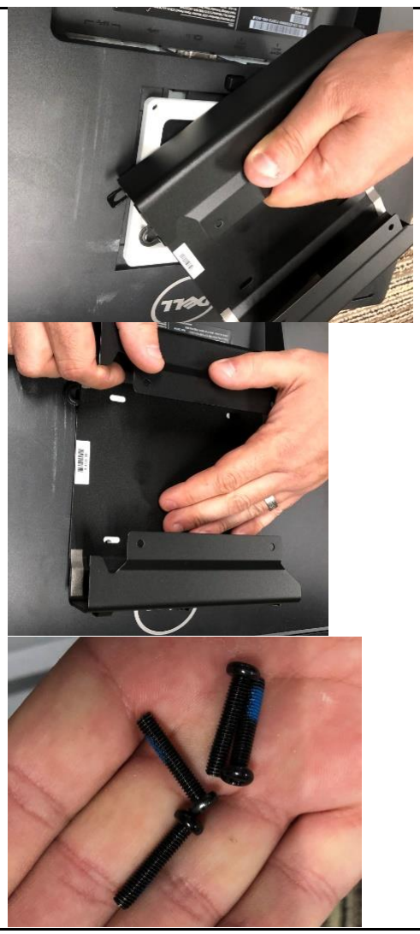
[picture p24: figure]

| NOTE: the screwdriver may not fit through the access holes above the screws. You may need to use a smaller screwdriver.

Actual screws

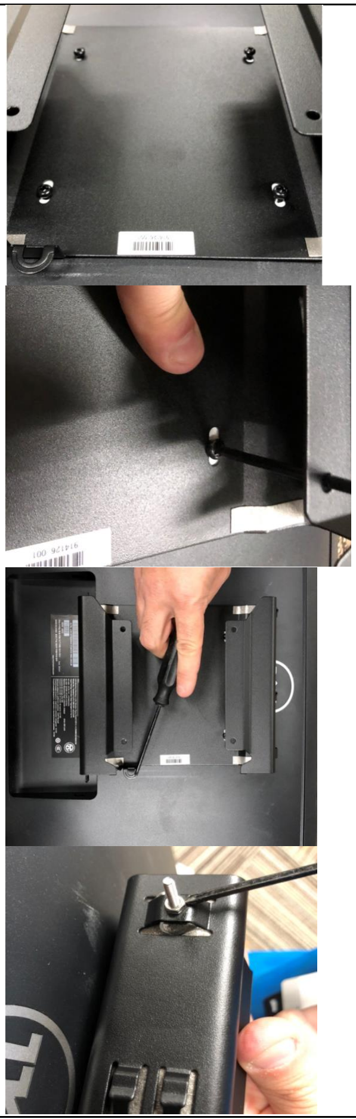
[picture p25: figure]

2.3.1.1 Be sure to center the screws in the VESA sleeve

NOTE: the mounting screw for the camera bracket is at the top and should be aligned with the top of the monitor.

2.3.2 | VESA sleeve lock goes to the bottom right of the monitor (See photo)
2.3.3 | Create hole in the tape on the inside of the
VESA sleeve (inside side, near raised mounting bracket) and push a M3 14mm screw through it

2.3.3.1 Use an M3 nut (5mm) to secure on the VESA sleeve

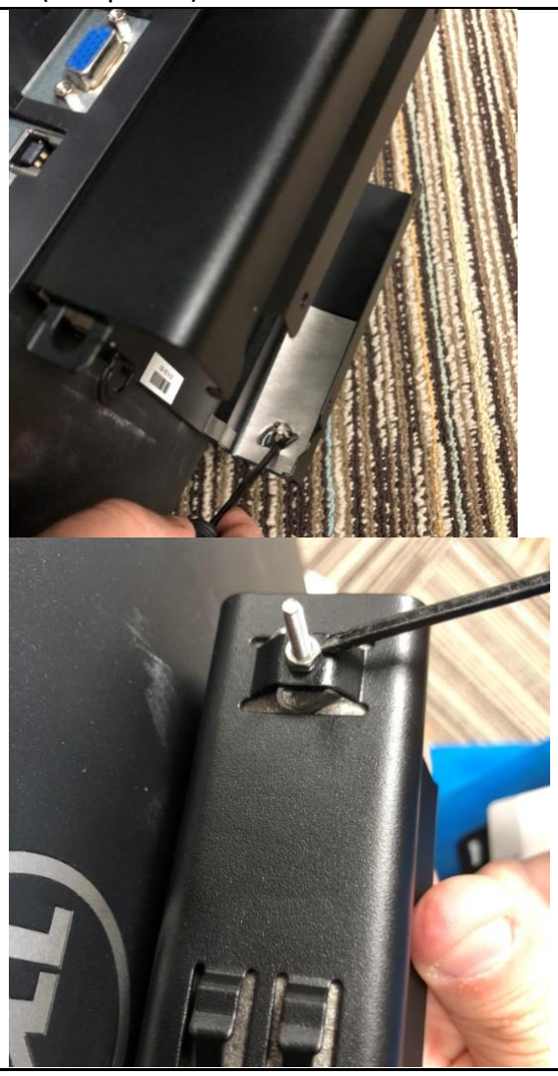
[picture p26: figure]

2.3.3.2 Note: a 2nd nut may be required during the support bracket alignment

2.4 Slide in the PC to the VESA sleeve

NOTE: Place a cloth or protective material between the monitor and surface to avoid scratching the monitor.

2.4.1 | Align the tripod VESAmount to the VESA sleeve to align the holes with the PC

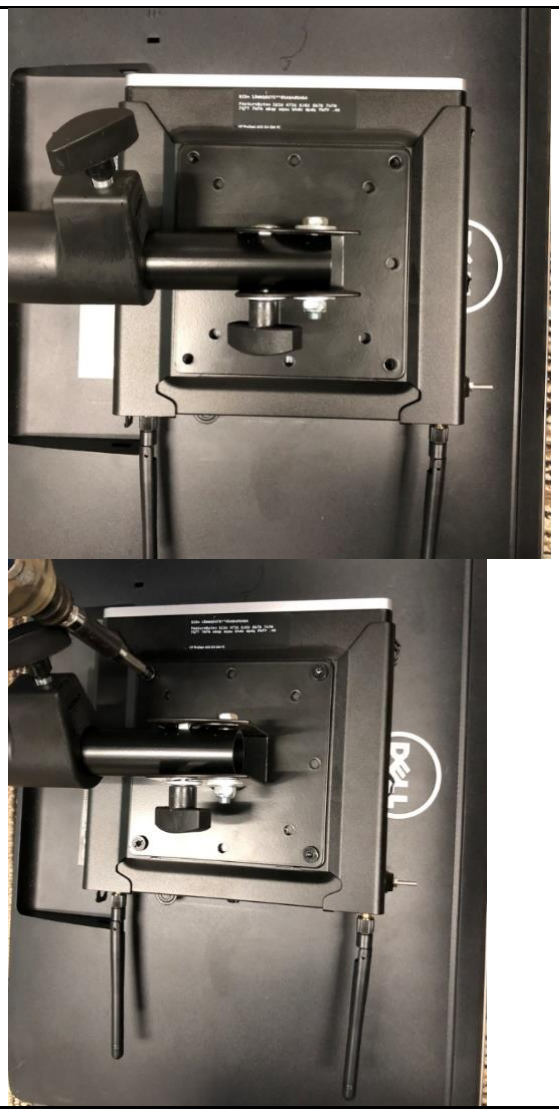
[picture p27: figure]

2.4.2 | Use M4 T15 screws provided in the VESA sleeve kit to connect the tripod and PC as one unit (be
careful to not over tighten) Note: the kit comes with two types and either can be used
2.4.3 Stand up the tripod

## 3. CAMERA BRACKET ASSEMBLY

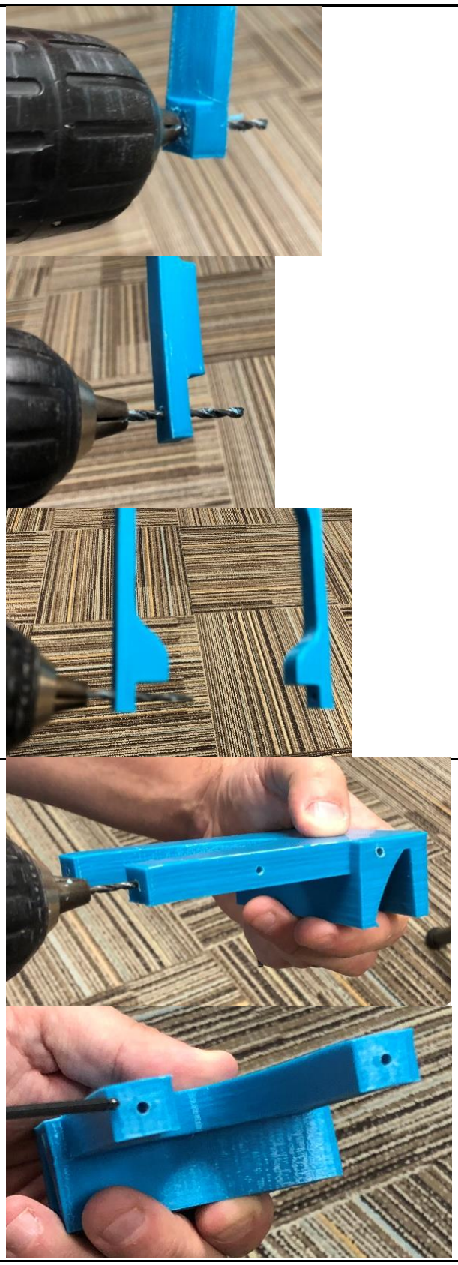
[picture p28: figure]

3.1 | Predrill the top and back brackets with a 1/8-inch drill bit (both sides, total of 4 holes)
3.2 | Predrill 5 holes on the camera bracket body with 3/32-inch drill bit and approximately ¼” deep

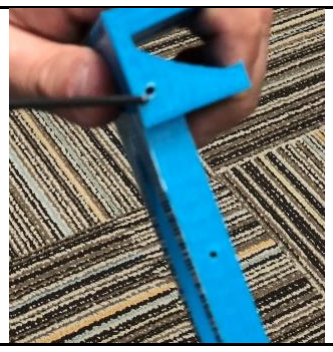
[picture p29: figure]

3.3 Attach the top bracket to the bracket body using M3 14mm screws. Pressure is required to self-tap.
3.3.1 Note: the top bracket has an angle that needs to slope towards the front of the bracket body

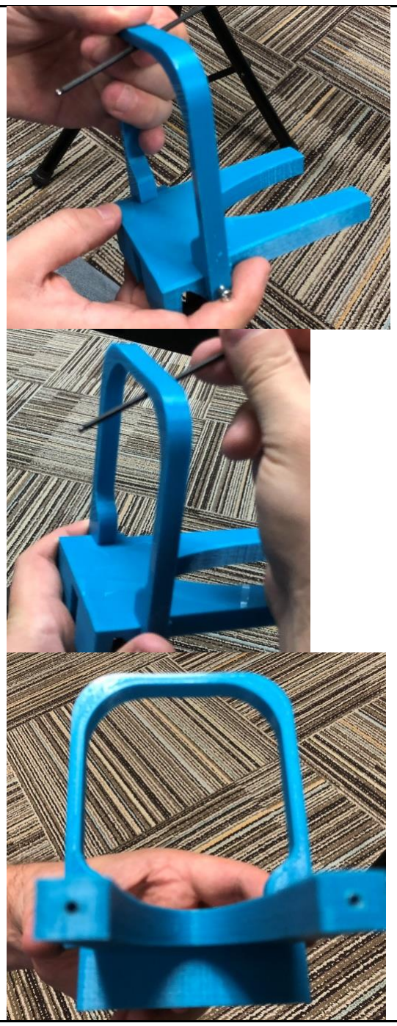
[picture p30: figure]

NOTE: a newer version of the top bracket will have a small ridge under the top arch. This small ridge goes to the back, away from the monitor.

3.4 | Ensure the camera lens cover is closed
3.5 | Mount the FLIR E8-XT series camera into the bracket, align the back of the top bracket to the front of the rubber flap on the camera

3.6 | Attach the back bracket (The draft angles to the handle on the camera) to the bracket body to secure the camera in place using M3 4mm screws

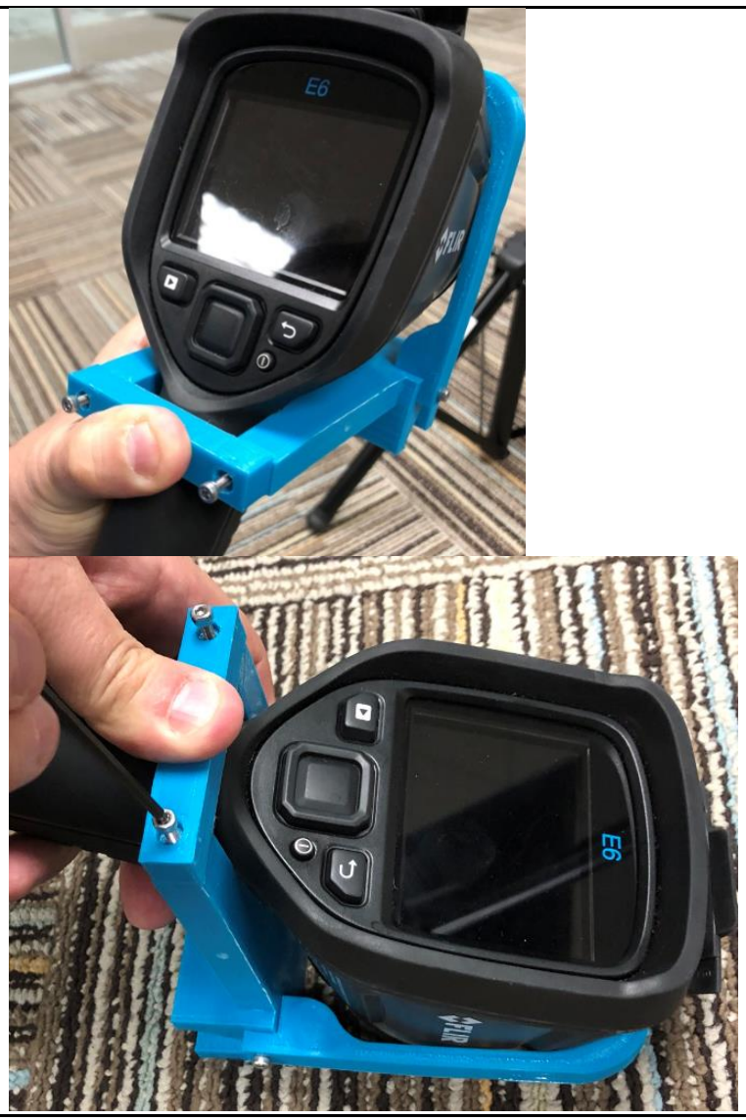
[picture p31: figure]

3.6.1 | Pressure will be required to push the camera forward in to the bracket body
3.6.2 | Pressure is required while screwing in to self-tap.
3.6.3 | You may need to squeeze the bracket body to align the holes with the back bracket
3.7 | Push the camera forward to ensure the rubber flap is aligned with the top bracket
3.7.1 | Check alignment from the front to
ensure the camera is centered in the
bracket

3.8 | Slide the camera on the top of the monitor and ensure it is center.
3.8.1 | The camera body mass is on the back of the monitor (See photo)
3.8.2 | The front of the bracket body has an
opening for the monitor camera (See
photo)

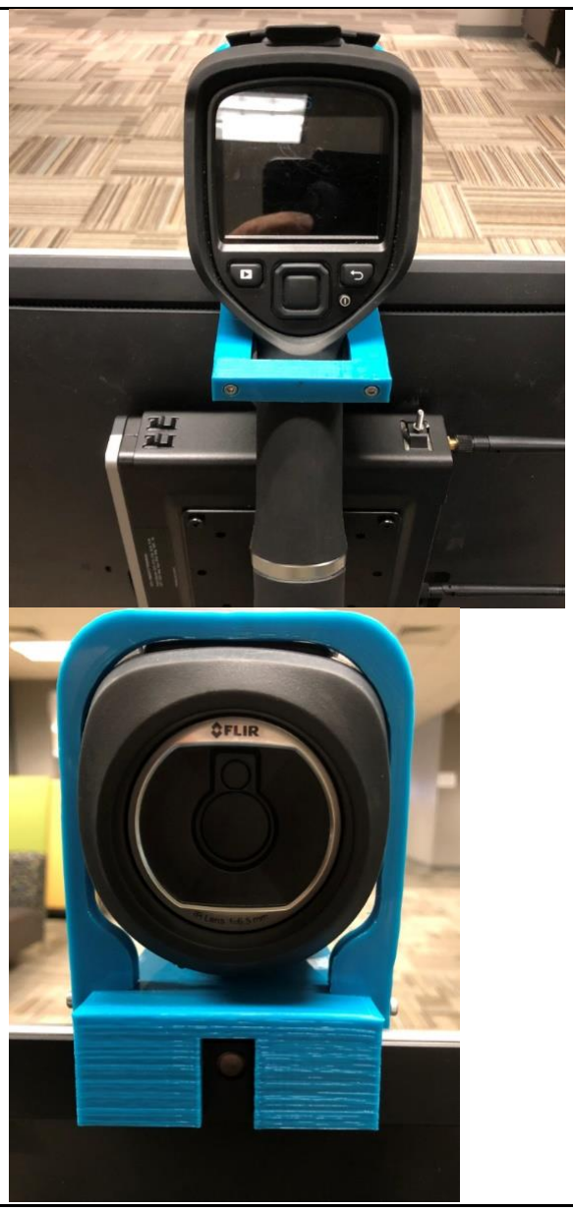
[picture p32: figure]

3.9 | Attach the support bracket to the bracket body and the VESA sleeve
3.9.1 | Using the remaining small metal nut, attach the bottom of the bracket to the screw
previously installed on the VESA sleeve and tighten
3.9.2 | Note: a second nut may be required under the bracket for proper alignment
3.9.3 | Use one of the supplied small screws to secure the top of the support bracket to the
bracket base. Pressure is required to self tap.

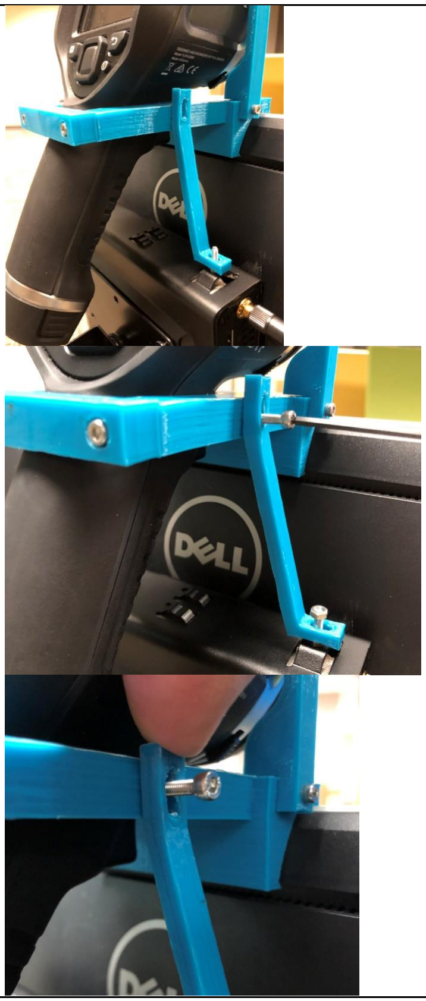
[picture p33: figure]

3.9.3.1.1 Center the screw in the slot on the top support (See photo)

NOTE: This slot will be used later to align the camera in “Section 6.4.1”

## 4. CABLE MANAGEMENT

### THE GOAL IS TO SECURE THE WIRES AND POWER SUPPLIES TO REDUCE THE TRIPPING HAZARD

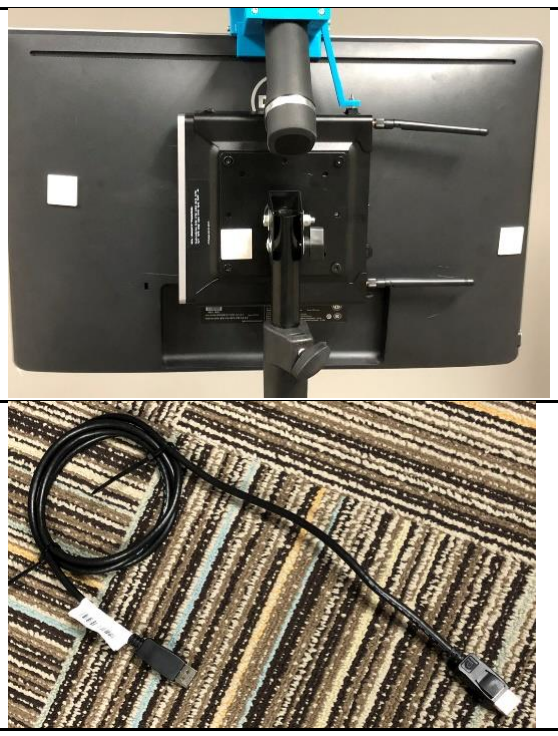
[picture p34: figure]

4.1 Attach 1X1 mounting bases on the back of the monitor and VESA sleeve (See photo)

4.2 Configure display port cable per the photo, approximately 6 inches on one end and one foot on the other end. Using zip ties after connecting all wires can help.

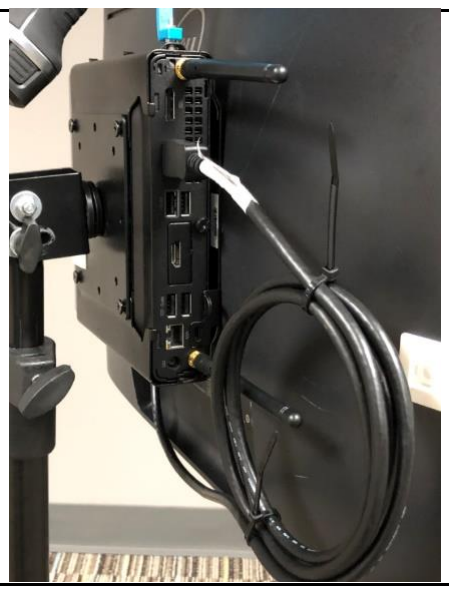
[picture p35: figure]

4.2.1 Attach to the monitor and PC as displayed in the photo. Use the second display port down on the PC

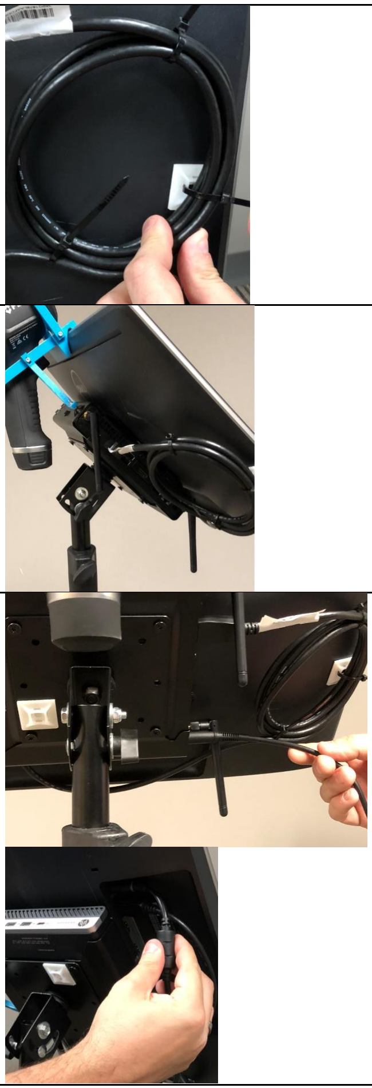
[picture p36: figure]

4.2.2 Secure the cable to a 1X1 mounting base with a zip tie

4.2.3 Ensure the wireless antenna is not behind the cable. Antennas are intended to be free so as to be vertical when the monitor is tilted

4.3 Install the HP Desktop PC and Dell Monitor power supplies(See photos)

The monitor is tilted in this picture to show the bottom and where the power supply connects.

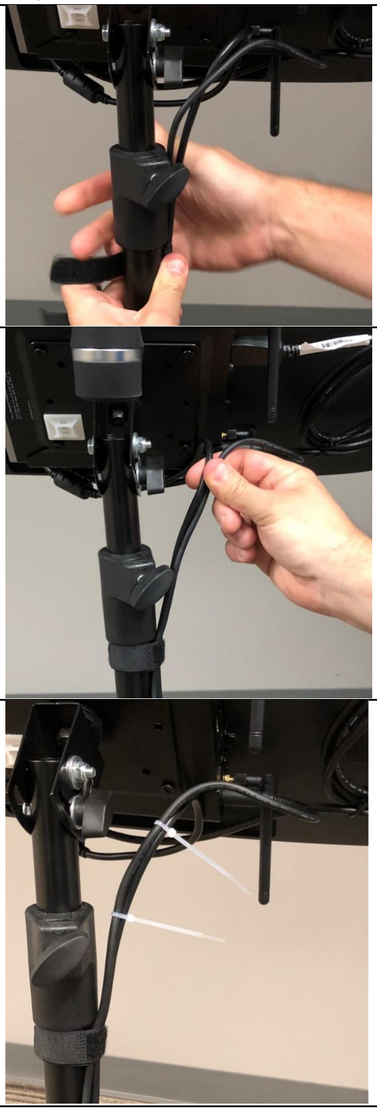
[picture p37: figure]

4.3.1 Using the Velcro strap to secure power cords to the tripod base 4.3.1.1 NOTE: The power wires go to the right of the vertical adjustable height wing nut

4.3.2 Leave enough slack for the monitor to tilt

4.3.3 Zip tie power cords and note the lower antenna is behind the PC power plug (See photo)

4.3.1 | Use two 8-inch zip ties to secure power cords to tripod base
| Take note of section 4.3.6 as you zip tie the power wires to the tripod.

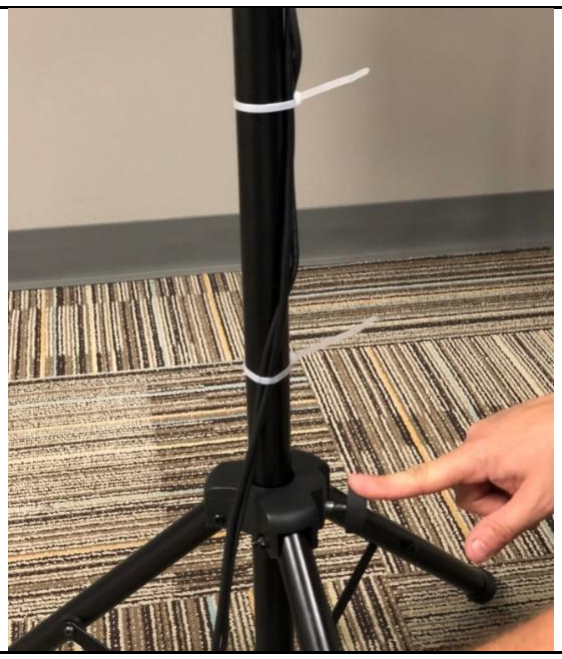
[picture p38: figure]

4.3.2 | Ensure the power cords come off the opposite side of the leg where the tripod base thumb screw
is located
4.3.3 Arrange the power bricks at the base of the tripod and secure to the tripod leg using the Dell strap.
NOTE: You may need to use a couple zip ties to secure the power supplies.

4.4 | Configure the USB A to USB B cable per the photo with approximately 6 inches on the A side and one foot on the B side

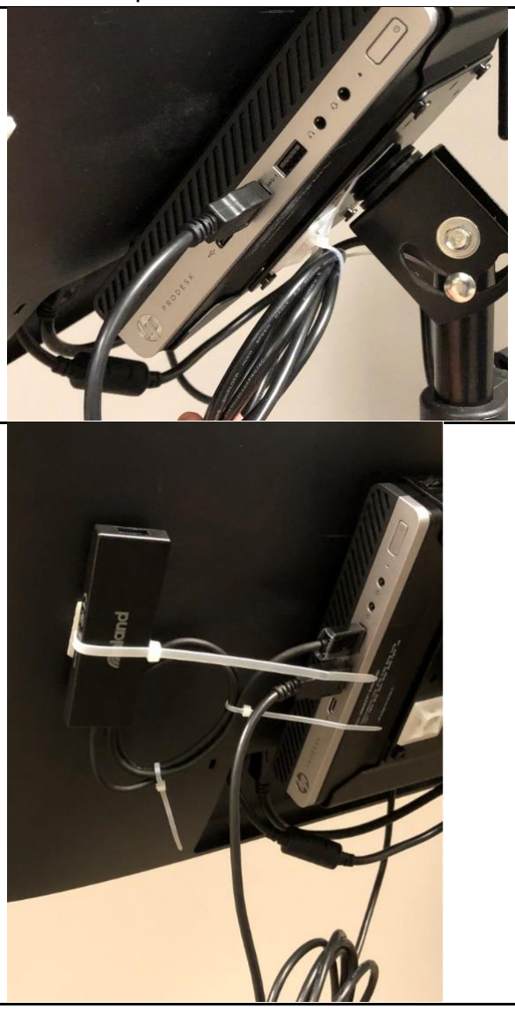
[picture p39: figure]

4.4.1 | Attach the USB A side to the second USB port away from the PC power button
4.4.2 Attach the USB B side to the USB B port on the bottom of the monitor The USB B end is square-shaped and the USB A end is flat.

4.5 Secure USB 3.0 hub to the 1X1 mounting base on the left side (Rear) of the monitor

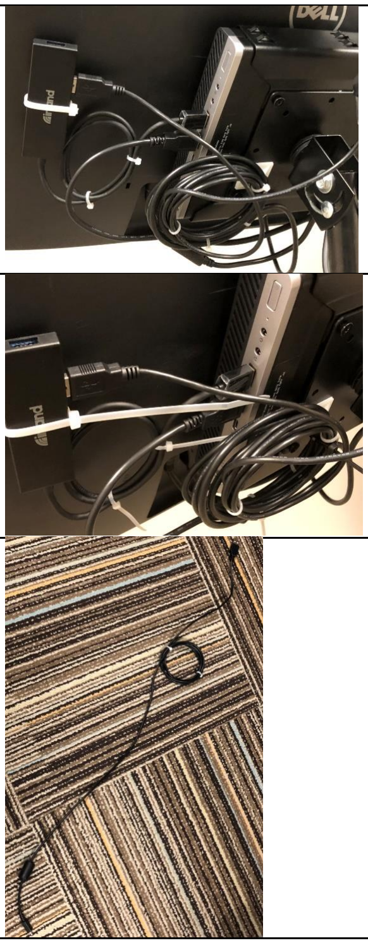
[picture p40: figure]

4.5.1 Zip tie the spooled cable to the USB cable installed in Step 4

4.5.2 Plug the USB A into the first USB port next to the PC power button

4.6 Configure the Micro USB to USB A cable (See photo) with 20 inches on the Micro USB end and 10 inches on the USB A end NOTE: This cable is packaged with the FLIR camera.

4.6.1 | Attach the micro USB end to the FLIR camera top (under the camera flap)

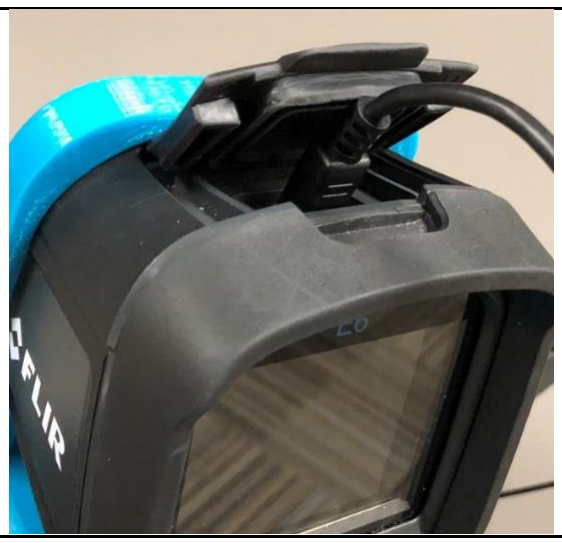
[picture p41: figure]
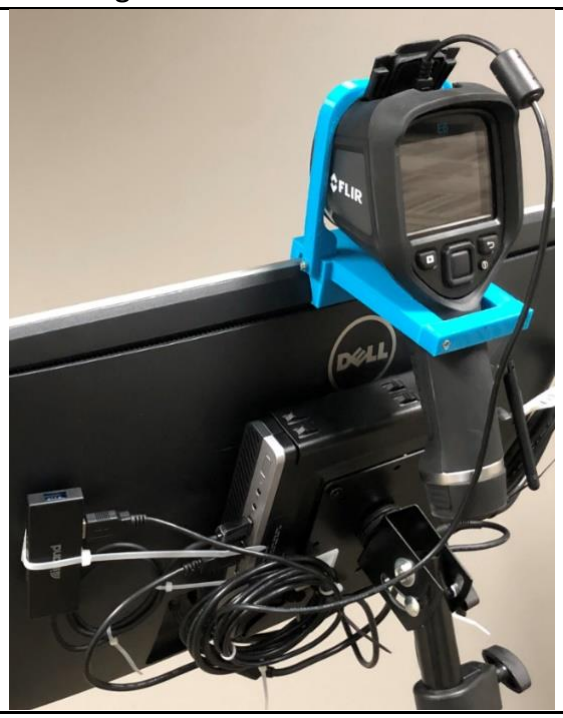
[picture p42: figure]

4.6.2 | Secure both USB cable loops to the VESA sleeve 1X1 mounting base
4.6.3 | Attach the USB A end to the USB 3.0 hub
4.7 | Trim zip ties

## 5. OPERATION

5.1 Adjust tripod tilt to a 45 degree angle

5.2 Lower the top tube all the way down and secure with thumb knob NOTE: This can be adjusted higher to help when evaluating taller individuals

5.3 Align the monitor to be center on the two front legs to reduce tripping hazard

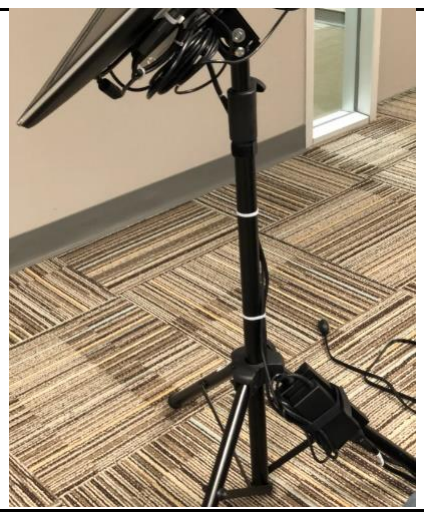
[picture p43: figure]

NOTE: lower the top all the way to the bottom and extended the legs all the way out Extend the legs as far as you can to help stabilize the tripod. Take note the power supplies are connected and will need room. Be sure to tighten all thumb knobs on the top and bottom

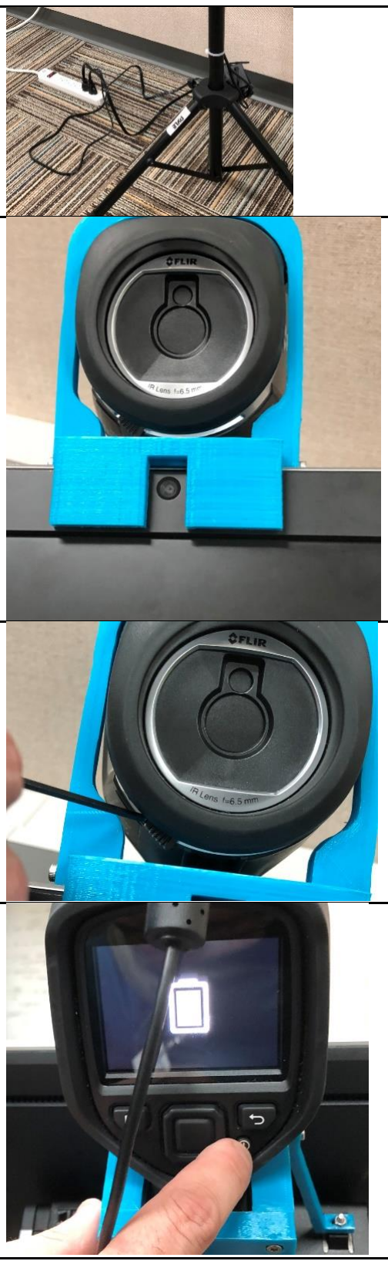
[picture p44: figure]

5.4 Plug in the HP and Dell power cords into a surge protector

5.5 Check the monitor camera alignment to ensure it is in the center of the bracket base opening (front of monitor)

5.6 Open the lens cover using the lens cover slide at the bottom of the FLIR camera NOTE: you can use the small allen key to open the lens cover

5.7 Power on the FLIR camera by depressing the power button located on the back-bottom right of the camera

5.7.1 The camera screen will show the front area once booting completes

5.8 Press the PC power button and the computer will boot up

5.8.1 NOTE: You may need to adjust the monitor input for the correct HDMI port you used You can cycle the input on the monitor until the desktop is displayed

5.8.2 It may take up to 10 seconds for the FLIR camera to be recognized once the software starts

5.9 Position the kiosk to avoid bright lights in the background (See photo)

5.9.1 Bright lights can cause a glow behind the user and impact the scan

5.10 User approaches the kiosk within 3 to 5 feet

5.10.1 Scan starts once the blue box is around the user face

5.10.2 User should remove hat and glasses 5.10.3 If facial detection fails, user may try lowering their mask below their nose and/or moving slightly closure to the kiosk

## 6. CAMERA AND SOFTWARE ALIGNMENT MODE

6.1 Attach a mouse to the USB hub being careful not to disrupt the camera USB connection

6.2 Click the shaded rectangle in the upper right corner to enable debug mode

6.3 Check that the thermal image box (right image) is aligned to the user’s eyes and forehead.

6.4 Large alignment issues may indicate the FLIR camera is not aligned to the monitor camera

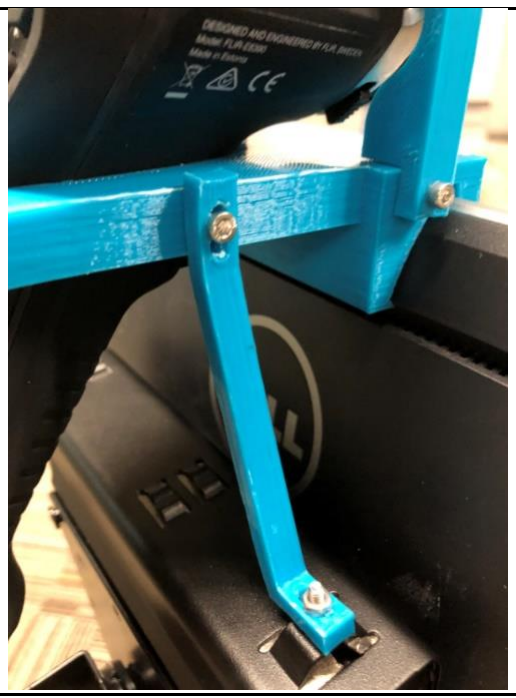
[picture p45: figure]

6.4.1 Check the camera and bracket base for coarse alignment and adjust as needed

6.5 Small adjustments can be made using the X and Y adjustments in debug mode

6.5.1 Plug in a USB keyboard to an available USB port on the PC being careful not to disrupt the other connections

6.5.2 Small horizontal offset is adjusted by changing the X setting. In this example, by changing the X setting from 90 to 82

6.6 Debug mode can be used to see the temperature reading over average. (See photo). This is to be used for debugging purposes only. Do not display these numbers or use debugging mode during operation.

6.7 Exit debug mode by clicking “Save” to save any changes and then clicking the shaded rectangle in the upper right corner. Remove the keyboard and mouse prior to operation.

## 7. TROUBLESHOOTING

7.1 | Users are not scanning properly
7.1.1 | Ensure hot objects are not in the background (vehicles, plant equipment, lobby
monitors, reflective surfaces, bright lights, etc.).
7.1.2 Add an LED lighting source to the scanning area facing the subject. This will ensure their facial contours are being recognized as the area of interest, which then trigger the thermal scan.
7.1.3 Review the section on Environmental Considerations in the readme file for more suggestions.
7.2 | The thermal camera screen is frozen
7.2.1 | Cycle the camera on/off button.
7.2.2 | If cycling the power on/off button does not work, remove the battery from the camera,
put the battery back into the camera and power on the camera. Restart the kiosk computer (turn off the power strip and turn back on) once the thermal camera is powered back on.
7.3 | The kiosk computer shut down due to a power outage
7.3.1 | Once site power is restored, power off the thermal camera. Turn the power strip off to
the kiosk. Turn the thermal camera on and wait for the camera to boot up. Turn the power strip back on and press the power button on the computer.
7.4 | The scanning software does not launch
7.3.2 | The software can be manually launched by navigating to C:\Program Files\Kiosk and
executing “ThermalImagingKiosk.exe”.
7.5 | The kiosk has stopped scanning
7.3.3 | Reboot the system (monitor and computer) to reset. This may be done by unplugging
both power cords.

## 8. TERMS OF USE

By using this kiosk design and its associated software, you agree to the following:

- This kiosk design and its associated software may only be used for initial evaluation of multiple users entering a facility or other area.
- This kiosk design and its associated software can only be used to examine one user at a time.
- This kiosk design and its associated software will not be used to determine, diagnose ortreat any disease or condition, including COVID-19.
- This kiosk design and its associated software will not be used to determine if a user has a fever.

- This kiosk design and its associated software will not be used to provide a user with their temperature, or any number related to their temperature.
- This kiosk design and its associated software must notify a user when an elevated thermal measurement is determined and, if such a determination is made, that additional evaluation is required.
- This kiosk design and its associated software can only be used in an environment where further evaluation is available using an appropriate method, such as measurement with a non-contact infrared thermometer or a clinical grade contact thermometer.
- This kiosk design and its associated software cannot be used for a commercial purpose. This includes manufacturing a kiosk for a third party; marketing or selling a kiosk; requesting compensation for the use of a kiosk; renting or leasing a kiosk; and the like. This does not preclude you using the kiosk design and its associated software for internal use with employees, visitors, customers, students, and the like who may enter your facility.
- FLIR requires that the use of this App with a FLIR EST Camera or approved FLIR Device is intended for use only as a skin temperature measuring tool, and is not a medically-approved body temperature measurement device or a medical diagnostic tool.

This kiosk relies on a third-party thermal infrared camera to provide readings to the software. An appropriate camera must be selected and any instructions for the camera followed for proper functioning of the kiosk. FLIR has indicated that its E8 camera is generally suitable for skin temperature screening applications.

THIS KIOSK DESIGN AND ITS ASSOCIATED SOFTWARE ARE PROVIDED "AS IS", WITHOUT WARRANTY OF ANY KIND, EXPRESS OR IMPLIED, INCLUDING BUT NOT LIMITED TO THE WARRANTIES OF MERCHANTABILITY, FITNESS FOR A PARTICULAR PURPOSE, AND NONINFRINGEMENT. IN NO EVENT SHALL THE AUTHORS OR COPYRIGHT HOLDERS BE LIABLE FOR ANY CLAIM, DAMAGES, OR OTHER LIABILITY, WHETHER IN AN ACTION OF CONTRACT, TORT OR OTHERWISE, ARISING FROM, OUT OF, OR IN CONNECTION WITH THE KIOSK, SOFTWARE, OR THEIR USE.

## 9. LICENSE

The software described in this paper is offered under licenses at https://github.com/generalmotors/thermal-scanning-kiosk/LICENSE.

This documentation is licensed under a Creative Commons Attribution-NoDerivatives 4.0 International License. (https://creativecommons.org/licenses/by-nd/4.0/)

Designs for the 3D-printed camera bracket and 3D-printed gasket described in this documentation are licensed under a Creative Commons Attribution-ShareAlike 4.0 International License. (https://creativecommons.org/licenses/by-sa/4.0/)

Attribution: Copyright 2020 General Motors LLC

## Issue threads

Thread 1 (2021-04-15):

### ISSUE TITLE
Can I use the E4 camera In this project?

### ISSUE THREAD

**Issue by xiaocainiao72865** [generalmotors/thermal-scanning-kiosk#1]
I want to use FLIR E4 to reproduce the project, but the program stuck in looking for the camera. How can I do ? Please help me!

**Comment by jcurrie1234** [comment]
@xiaocainiao72865 the code is intentionally restricted to use the FLIR-E8 XT due to agreements with FLIR. FLIR has required this program to use the FLIR-E8 as they have stated that the E6 and E4 are not appropriate for this type of application as they will not provide the accuracy and resolution required.

**Comment by xiaocainiao72865** [comment]
> @xiaocainiao72865 the code is intentionally restricted to use the FLIR-E8 XT due to agreements with FLIR. FLIR has required this program to use the FLIR-E8 as they have stated that the E6 and E4 are not appropriate for this type of application as they will not provide the accuracy and resolution required.

Thank you for your answer. But unfortunately, I only have a FLIR E4 camera. I want to understand FLIR's workflow through reproduce the project in the postgraduate study. How can I remove the restriction in the project?

**Comment by dantelope** [comment]
@jcurrie1234 from a purely educational standpoint could we provide this?

**Comment by jcurrie1234** [comment]
I'm sorry that I can't help with your project, but providing information to bypass the intentional controls of this software would violate our agreement with FLIR and would violate the Terms of Use of this software, which can be found in the README file.

"FLIR requires that the use of this App with a FLIR EST Camera or approved FLIR Device is intended for use only as a skin temperature measuring tool, and is not a medically-approved body temperature measurement device or a medical diagnostic tool.

This kiosk relies on a third-party thermal infrared camera to provide readings to the software. An appropriate camera must be selected and any instructions for the camera followed for proper functioning of the kiosk. FLIR has indicated that its E8 camera is generally suitable for skin temperature screening applications."

**Comment by xiaocainiao72865** [comment]
It is very sad to hear this news. This is a wonderful program in GitHub, but unfortunately I can’t reproduce it with my E4. Thank you again for your generous help.

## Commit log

2020-08-05 Initial Release Version 1.0
    [Camera_mount_Blank_Body.stp, Camera_mount_Dell_UZ2215HF_Body.stl, Camera_mount_Dell_UZ2215HF_Body.stp, Camera_mount_Dell_UZ2215HF_Side.stl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]
2020-09-16 Update README.md
    Updated Bill of Materials estimated cost for the FLIR E8-XT Thermal Camera
2020-11-19 Camera_Mount_HP_LA2206xc Folder
2020-11-19 Add HP LA2206xc 3D Parts
    [Camera_Mount_HP_LA2206xc_Body.stl, Camera_Mount_HP_LA2206xc_Side.stl]
